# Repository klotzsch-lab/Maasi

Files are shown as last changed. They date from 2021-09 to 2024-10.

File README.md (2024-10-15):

  

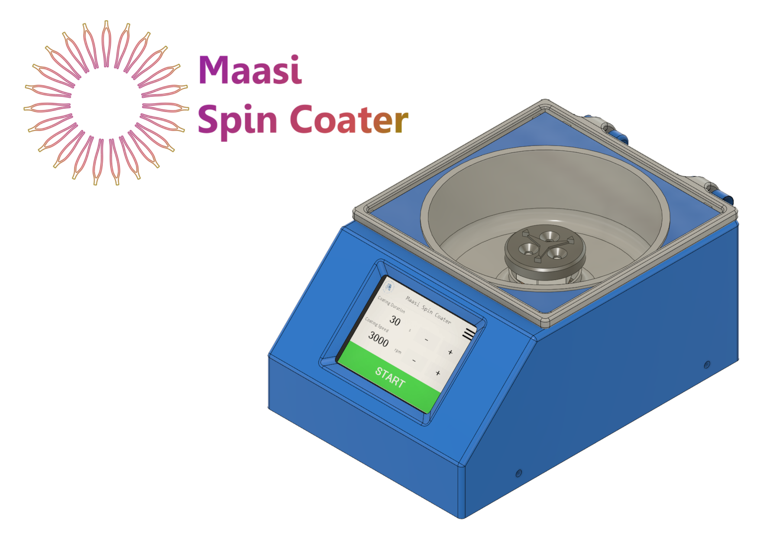
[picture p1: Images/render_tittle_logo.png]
poseidon_logo






## maasi: Open source spin coater

## WARNING!!!!! This project is no longer actively maintained. 

## Proceeding to build or use this project is at your own risk and responsibility.

A fully 3D printed, easy-to-use and open-source spin coater.

**Build tutorial**: https://www.youtube.com/watch?v=bhJrJDhlixs

**HardwareX Paper**: In review

## The tl;dr

Here we present Maasi, an affordable Spin Coater that is easy to build and has all functional key features to be used in a wide range of applications up to 8000 RPM. Our design has a price of approximately 85 € and an assembly time of 2 hours. One of the principles that guided the design was to use only 3D printed parts and affordable Commercial Off-The-Shelf (COTS) components. In order to keep a low part count we use an electronic speed controller (ESC) with telemetry, this eliminates the need for a rotor sensor.

using_maasi

## What is included?

* Computer Aided Design (CAD) files of the complete assembly.

* 3D printable .3MF files.

* Nextion Editor project for the Graphical user interface (GUI).

* Arduino firmware source files.

* Bill of materials for sourcing and purchasing materials.

* Detailed assembly instructions of hardware components.

## Getting Started

### 3D printing components and purchasing hardware

The 3D printed components can be fabricated on any desktop fused filament fabrication (FFF) 3D printer. They were designed using [Autodesk Fusion 360](http://autodesk.com/fusion360), a proprietary CAD software that offers free academic licenses.

- Fusion360 interactive view of [maasi spin coaterCAD](https://a360.co/3xFyf5n).

- Bill of materials with prices and vendor links on a [Spreadsheet](https://github.com/klotzsch-lab/Maasi/tree/main/doc/Maasi-BoM.ods).

- Print files (.3MF ) are available in the [/HARDWARE](https://github.com/klotzsch-lab/Maasi/tree/main/HARDWARE/) folder and print details are specified in the HardwareX publication.

### Build Video

Maasi v1: https://www.youtube.com/watch?v=bhJrJDhlixs&t=412s

Further build instructions are detaild in the HardwareX publication. The following is short version of those instrucitions.

### Setting up the ESP32

The ESP32 is the main MCU in Maasi. It coordinates the actions in the coating process and comunicates with the ESC and the Display MCUs.

Use the Arduino IDE to compile and flash the ESP32 (DevKitc V4)

 <strong>IMPORTANT: </strong> Users are experiencing problems (unresponsive touchscreen) with the Arduino ESP32 [v1.0.5](https://github.com/espressif/arduino-esp32/releases) and above. Please use the Board Manager to install v1.0.4 or previous until a fix is released.

**Make sure to install the following libraries**

-  [Nextion library](https://github.com/klotzsch-lab/Maasi/tree/main/SOFTWARE/Arduino/ITEADLIB_Arduino_Nextion). Included in this repository. To install, unzip the zip file to the libraries sub-folder of your sketchbook, if you get stuck here is a [how-to](https://www.arduino.cc/en/guide/libraries).

-  [PID_V1](https://github.com/br3ttb/Arduino-PID-Library)

-  [ElapsedMillis](https://www.arduino.cc/reference/en/libraries/elapsedmillis/)

### Setting up the Nextion Display

The display project was devoloped using Nextion Editor. We provide precompiled binaries if no customization is needed:

Copy into a micro SD card the file: [maasi_v1.tft](https://github.com/klotzsch-lab/Maasi/tree/main/SOFTWARE/Nextion/maasi_v1.tft)

Install the micro SD card in the Nextion display and power it up.

After the flashing process the SD card can be removed.

### Setting up the BLHeli_32 ESC

The ESC firmware is loaded using [BLHeliSuite32](https://github.com/bitdump/BLHeli/releases)

The required version for this project is the v32.7

An arduino UNO or nano is needed as flashing device between the PC and the ESC.

###  Putting together the Hardware
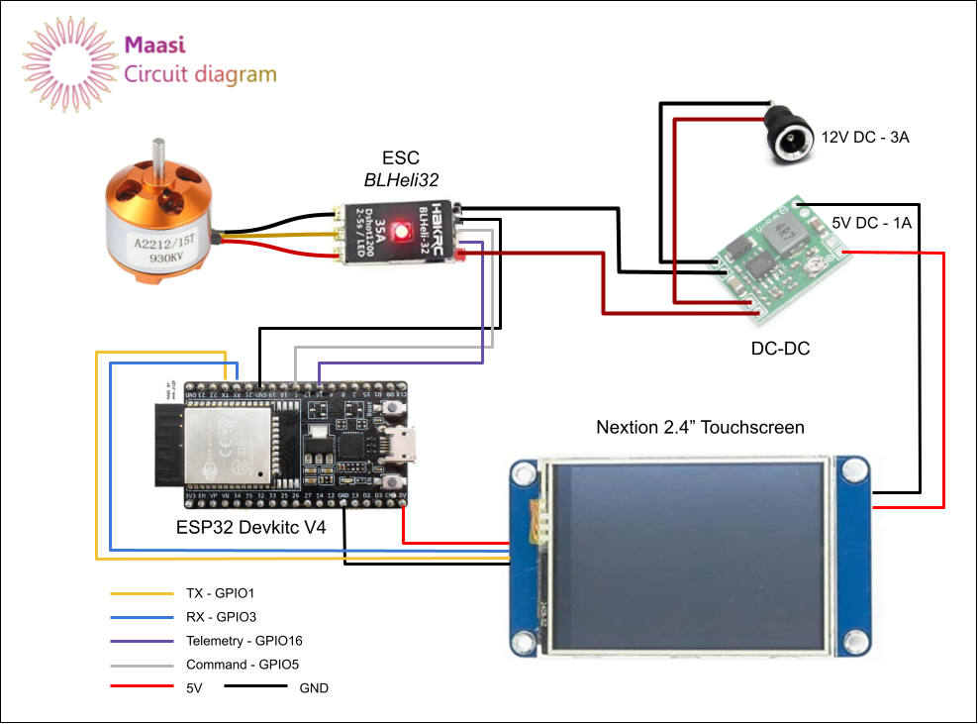
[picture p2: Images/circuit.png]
circuit_diagram_maasi


## Safety Considerations

Please review the license before using/developing/distribution maasi.

The maasi spin coater system uses 3D printed PLA plastic and standard off the shelf components which do not pose a health hazard if handled correctly. Improper handling of plastics however can create hazards when working with organic solvents.

The motor can spin at very high RPM and a safety lid was added to reduce the risk of injure in case that the substrate was not properly fixed to the holder.

Before using maasi in a wetlab environment, please ensure that you have thoroughly tested its functionality for your use case in a dry lab. Once the maasi system has been moved into a wetlab, it should not be moved back to a drylab or dry workbench.

If you plan to build on the maasi spin coater, ensure that you communicate any safety concerns that you may have with your design to potential users and collaborators.

## Authors

Maasi was developed by the [Klotzsch Lab](https://www.biologie.hu-berlin.de/en/groupsites/jpexpbp) at HU Berlin by:

-  [Dani Carbonell](https://github.com/dani-carbonell)

-  Willi Weber

-  [Enrico Klotzsch](https://www.biologie.hu-berlin.de/en/groupsites/jpexpbp/members/Enrico_Klotzsch)

#### Prior work and references

The maasi project is based on a number of other open source projects and papers.
A complete references list can be found inside the HardwareX paper.

The idea to use the ESC telemetry was based on the DIY spin coater built by [@BenKrasnow](https://www.youtube.com/watch?v=321tptQ8PrU) (Applied Science in Youtube)

The documentation format was largely inspired by [Pachter Lab](https://pachterlab.github.io/):

[Booeshaghi, A.S., Beltrame, E.d.V., Bannon, D. et al. Principles of open source bioinstrumentation applied to the poseidon syringe pump system. Sci Rep 9, 12385 (2019). https://doi.org/10.1038/s41598-019-48815-9](https://www.nature.com/articles/s41598-019-48815-9)

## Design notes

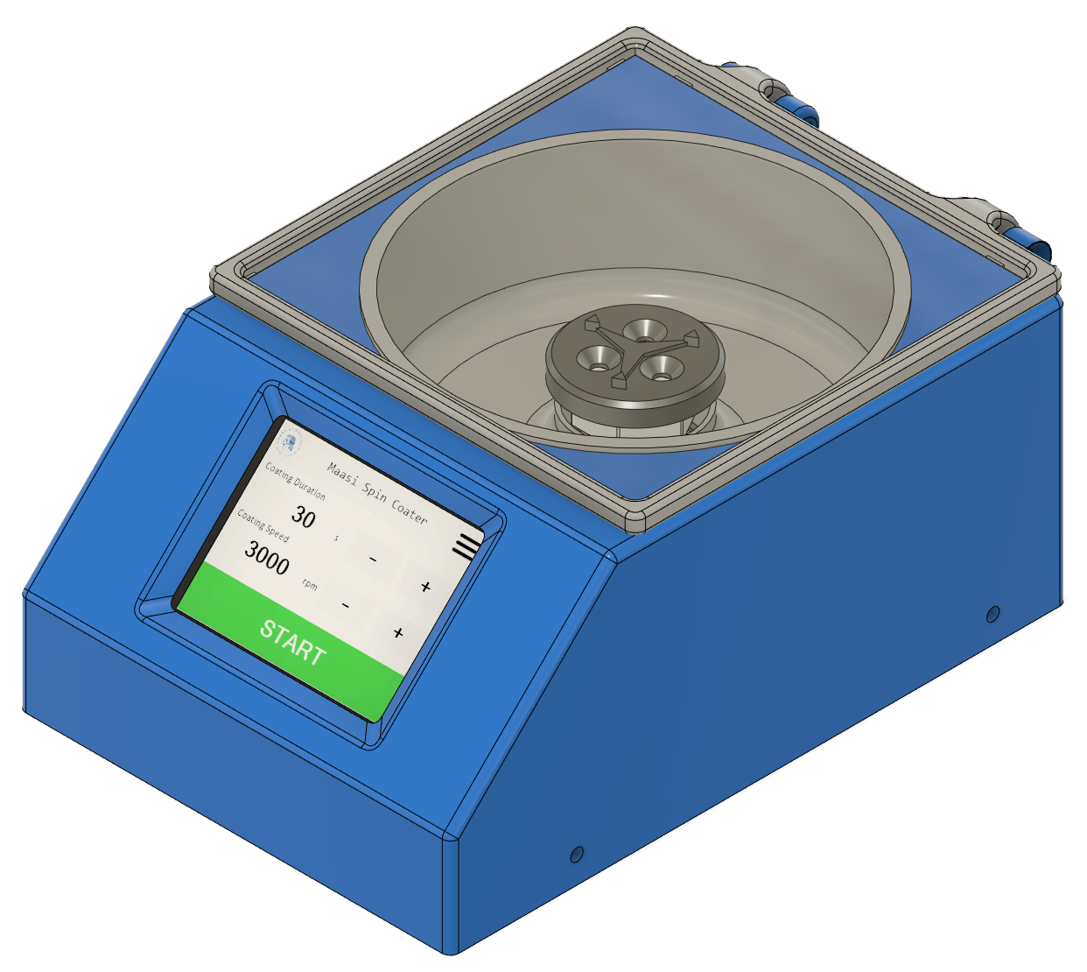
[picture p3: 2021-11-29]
Images/render.png

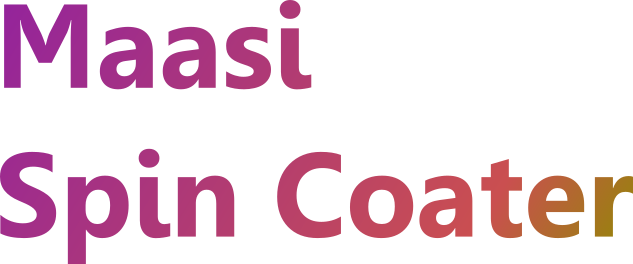
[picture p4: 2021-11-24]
Images/maasi_tittle.png

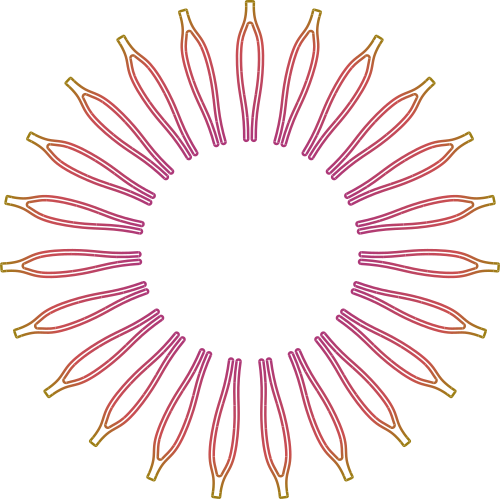
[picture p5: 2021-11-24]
Images/maasi_fusion360_500.png

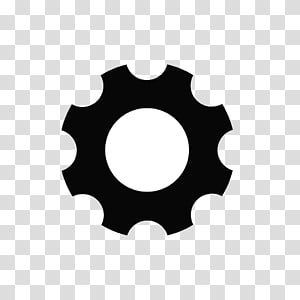
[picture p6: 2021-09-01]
SOFTWARE/Nextion/images/5a95ed98d4fc01607e5e6eb79c2b0c93.jpg

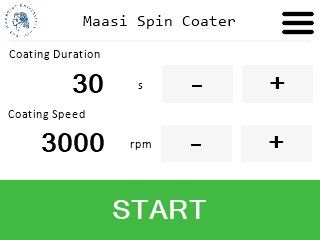
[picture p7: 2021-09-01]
SOFTWARE/Nextion/mainscreen_render.png

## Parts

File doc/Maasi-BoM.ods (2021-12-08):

Designator | Component | Number | Unit | Cost per unit - € | Total cost - € | Source of materials | Material type
PN_001 | BLDC Motor - A2212 - KV930 | 1 |  | 5.87 € | 5.87 € | Aliexpress (https://es.aliexpress.com/item/4001196428994.html) | Composite
PN_002 | ESC - Turnigy MultiStar BLheli_32 ARM 41A | 1 |  | 16.27 € | 16.27 € | HobbyKing (https://hobbyking.com/es_es/turnigy-multistar-32bit-41a-race-spec-esc-2-5s-opto.html?queryID=4c45ede8fe5c60a30a5b7e1fe6d4556b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) | Composite
PN_003 | Mini DC-DC - 12V to 5V | 1 |  | 0.50 € | 0.50 € | Aliexpress (https://es.aliexpress.com/item/32952187058.html) | Composite
PN_004 | ESP32 Devkit v4 | 1 |  | 6.35 € | 6.35 € | Aliexpress (https://es.aliexpress.com/item/1005001838731651.html) | Composite
PN_005 | Nextion NX2432T024 - Touchscreen 2,4" | 1 |  | 23.00 € | 23.00 € | Aliexpress (https://es.aliexpress.com/item/32833690695.html) | Composite
PN_006 | Jack Panel Mount Connector 5.5*2.1mm | 1 |  | 0.70 € | 0.70 € | Aliexpress (https://es.aliexpress.com/item/32985876868.html) | Plastic-Metal
PN_007 | PLA filament | 0.4 | Kg | 20.00 € | 8.00 € | Aliexpress (https://es.aliexpress.com/item/1005003572215645.html) | Plastic
PN_008 | Rubber Feet - 20x16x10mm | 4 |  | 0.18 € | 0.72 € | Aliexpress (https://es.aliexpress.com/item/4000835196671.html) | Rubber-Metal
PN_009 | M3x10 bolts (case) | 4 |  | 0.20 € | 0.80 € | Aliexpress (https://www.aliexpress.com/item/33022099174.html) | Metal
PN_010 | M3x12 bolts (feet) | 4 |  | 0.20 € | 0.80 € | Aliexpress (https://www.aliexpress.com/item/33022099174.html) | Metal
PN_011 | M3x12 bolts (screen) | 4 |  | 0.20 € | 0.80 € | Aliexpress (https://www.aliexpress.com/item/33022099174.html) | Metal
PN_012 | 100x100mm 3mm Transparent Plexiglass | 1 |  | 4.23 € | 4.23 € | Aliexpress (https://www.aliexpress.com/item/4000388406779.html) | Plexiglass
PN_013 | Soldering Tin Lead Free | 5 | g | 0.08 € | 0.42 € | Aliexpress (https://www.aliexpress.com/item/32824531083.html) | Tin
PN_014 | 22AWG Cable (Black-Red) | 0.4 | m | 0.33 € | 0.13 € | Aliexpress (https://www.aliexpress.com/item/4000689875049.html) | Copper-PVC
PN_015 | 12V 5A - AC-DC Power adapter | 1 |  | 10.00 € | 10.00 € | Aliexpress (https://es.aliexpress.com/item/32859196804.html) | Composite
PN_016 | Hook and Loop Fastener Tape 20mm | 0.1 | m | 3.17 € | 0.32 € | Aliexpress (https://es.aliexpress.com/item/33036100627.html) | Nylon
PN_017 | M3 X D4.2 X L5.0 Brass Hot Melt Insert Nuts | 6 |  | 0.08 € | 0.50 € | Aliexpress (https://www.aliexpress.com/item/4000909684199.html) | Metal
PN_018 | M4x20 bolts - Countersunk Head | 2 |  | 0.12 € | 0.24 € | Aliexpress (https://es.aliexpress.com/item/4000020967604.html) | Metal
PN_019 | M3x8 bolts - Countersunk Head | 3 |  | 0.03 € | 0.09 € | Aliexpress (https://es.aliexpress.com/item/4000020967604.html) | Metal
 |  |  |  | TOTAL | 79.73 €
 | Alternatives
Designator | Component | Number | Unit | Cost per unit - EUR | Total cost - EUR | Source of materials | Material type
PN_002_alt1 | ESC - HAKRC BLHeli32 dshot1200 35A | 1 |  | 22.94 € | 22.94 € | Aliexpress (https://es.aliexpress.com/item/4001176494750.html) | Composite
 | Hardware Tools
 | FFF 3D Printer (min. volume 110x160x70mm)
 | Screwdrivers
 | Cutting Pliers
 | Soldering iron
 | Allen Keys
 | Windows 10 Computer with micro SD reader
 | Jumper wires
 | Arduino Uno or Nano
 | Micro SD card
 | Software tools
 | Arduino IDE 1.8
 | BLHeliSuite32
 | Nextion Editor (Optional)
 | Autodesk Fusion 360 (Optional)

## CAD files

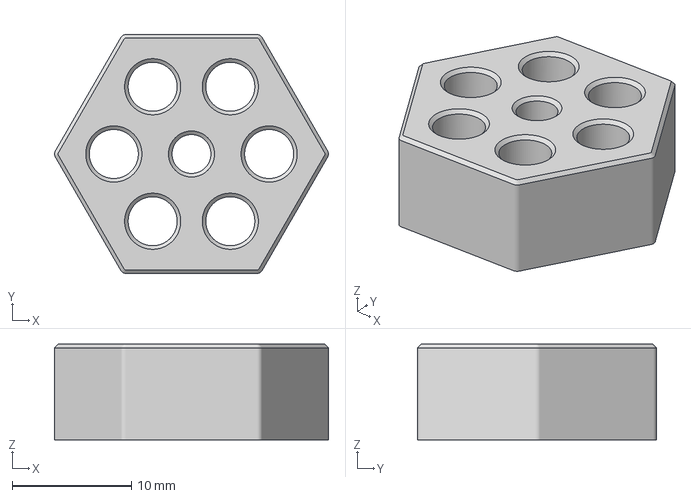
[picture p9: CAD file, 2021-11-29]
HARDWARE/3mf/Shaft_adapter.3mf
22.9 x 20.0 x 8.00 mm

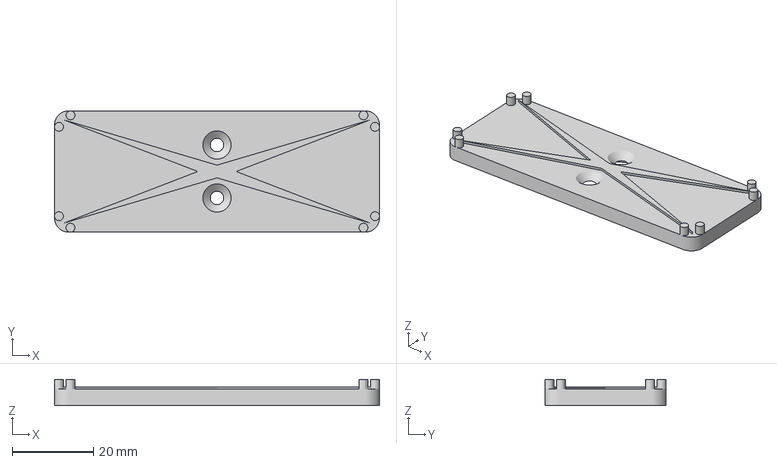
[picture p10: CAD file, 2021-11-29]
HARDWARE/3mf/Square_holder_75x25.3mf
79.8 x 29.8 x 6.40 mm

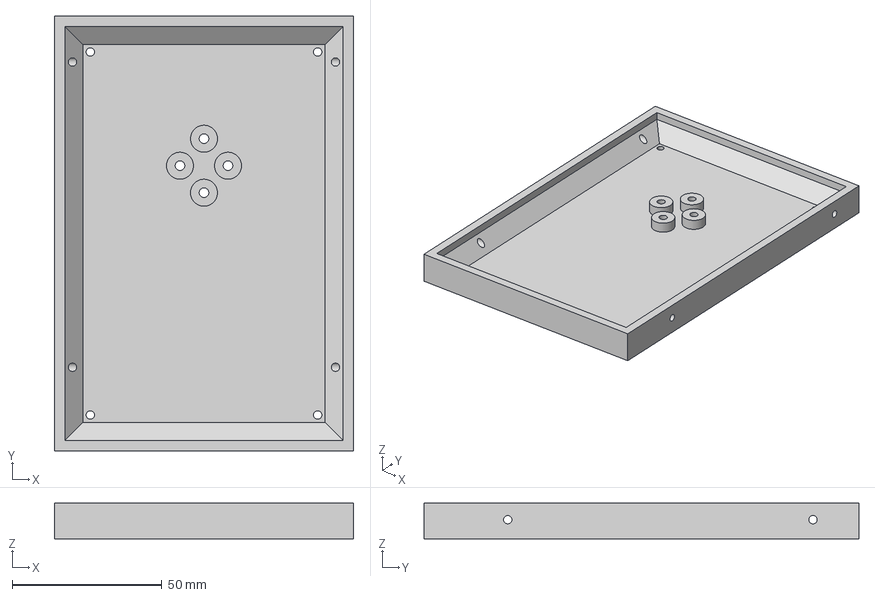
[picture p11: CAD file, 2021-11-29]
HARDWARE/3mf/Base.3mf
99.8 x 145.0 x 12.0 mm

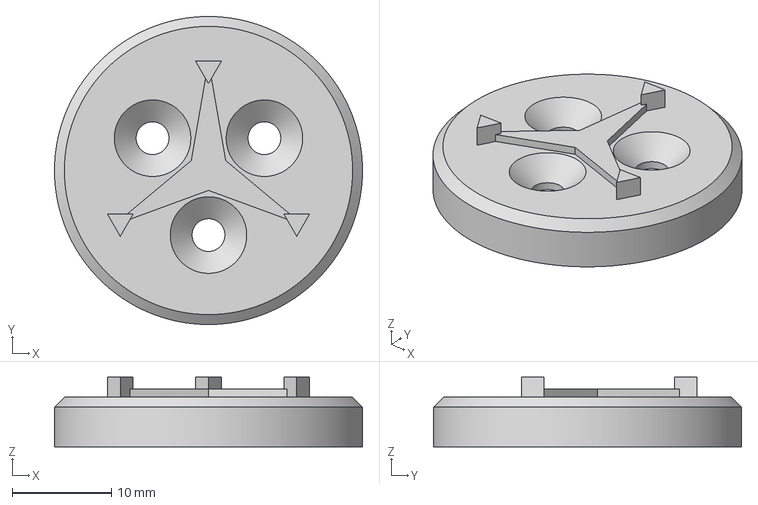
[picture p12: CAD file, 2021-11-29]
HARDWARE/3mf/Round_holder_18mm.3mf
31.0 x 31.0 x 7.00 mm

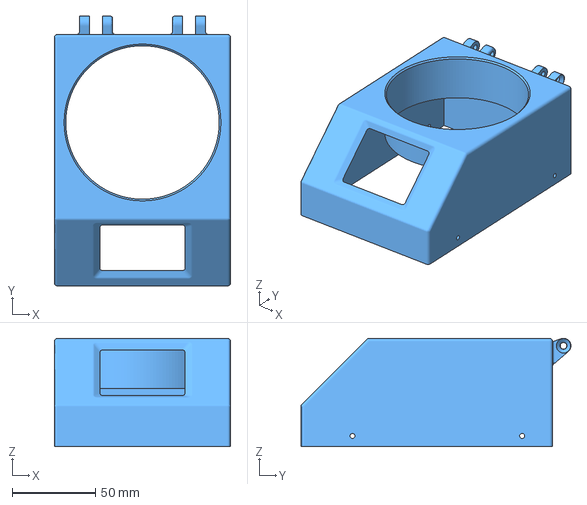
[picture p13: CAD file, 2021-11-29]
HARDWARE/3mf/Case.3mf
105.8 x 162.0 x 65.0 mm

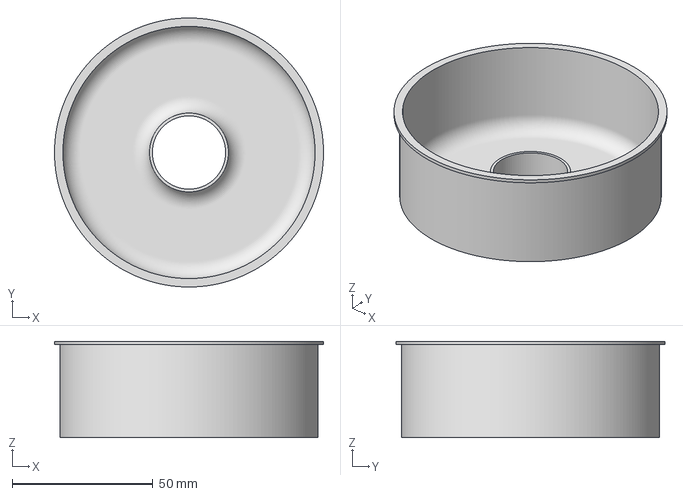
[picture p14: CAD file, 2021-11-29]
HARDWARE/3mf/Vase.3mf
95.5 x 95.5 x 34.2 mm

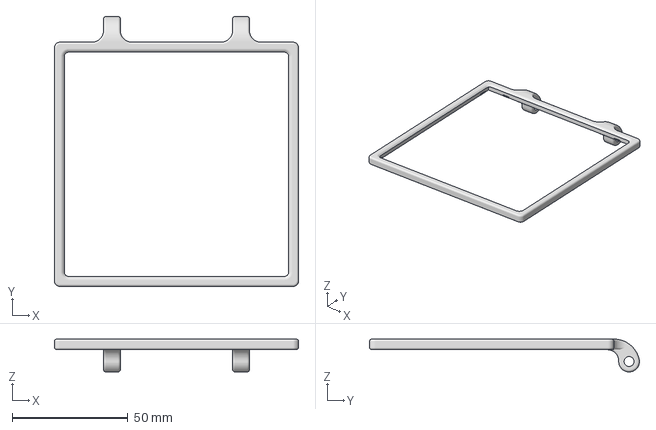
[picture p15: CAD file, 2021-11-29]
HARDWARE/3mf/Lid_frame_hinges.3mf
105.6 x 116.7 x 14.2 mm

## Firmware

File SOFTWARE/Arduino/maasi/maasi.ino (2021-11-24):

#include <HardwareSerial.h>
#include "freertos/FreeRTOS.h"
#include "freertos/task.h"
#include "freertos/event_groups.h"
#include "Arduino.h"
#include "esp32-hal.h"
#include "nextion_hmi.h"
#include <elapsedMillis.h>
#include <PID_v1.h>


#define DEFAULT_DISPENSE_SPEED 600       // RPM
#define DEFAULT_COAT_SPEED 3000          
#define MIN_COAT_SPEED 300
#define MAX_COAT_SPEED 8000
#define INCREMETS_COAT_SPEED 100



#define DEFAULT_COAT_TIME 30000 // In ms
#define MIN_COAT_TIME 1000
#define MAX_COAT_TIME 80000
#define INCREMETS_COAT_TIME 1000
#define DEFAULT_RAMPUP_TIME 3000
#define MIN_RAMPUP_TIME 1000
#define MAX_RAMPUP_TIME 6000
#define DEFAULT_RAMPDOWN_TIME 1500
#define MIN_RAMPDOWN_TIME 500
#define MAX_RAMPDOWN_TIME 5000

#define MOTOR_POLE_PAIRS 7

#define GREY 54970
#define GREEN 17864


//---------------------------------------
//  Coating params
//---------------------------------------

uint16_t disp_speed, coat_speed;

int32_t rampup_time, rampdown_time, coat_time;

enum state {
  STATE_IDLE,
  STATE_DISPENSING,
  STATE_RAMPUP,
  STATE_RAMPDOWN,
  STATE_COATING
};

state current_state, previous_state = STATE_IDLE;

//----------------------------------------------------------------------------
// Espressif Infrared Remote(rmt) library is used to create DSHOT messages in a fast manner
//-----------------------------------------------------------------------------

TaskHandle_t Task1;

rmt_data_t dshotPacket[16];
rmt_obj_t* rmt_send = NULL;

hw_timer_t * timer = NULL;

HardwareSerial TelSerial(1);

// ESC Telemetry variables
uint8_t receivedBytes = 0;
volatile bool requestTelemetry = false;
int16_t ESC_telemetry[5]; // Temperature, Voltage, Current, used mAh, eRpM
//uint32_t telemetry_fails = 0;
//uint32_t telemetry_succ = 0;


uint32_t currentTime;
uint8_t temperature = 0;
uint8_t temperatureMax = 0;
float voltage = 0;
float voltageMin = 99;
uint32_t current = 0;
uint32_t currentMax = 0;
uint32_t erpm = 0;
uint32_t erpmMax = 0;
uint32_t rpm = 0;
uint32_t rpmMAX = 0;
uint32_t kv = 0;
uint32_t kvMax = 0;

//---------------------------------------
//   PID parameters
//---------------------------------------
double motor_setRPM, motor_actualRPM, pid_output = 0;
double pid_out_min = 48;
double pid_out_max = 2047;
double Kp = 0.015, Ki = 0.8 , Kd = 0.0; // Before 1,3,0
const int sample_time = 1; //ms


PID motorPID(&motor_actualRPM, &pid_output, &motor_setRPM, Kp, Ki, Kd, DIRECT);


//---------------------------------------
//   ESC Control Parameters
//---------------------------------------

uint16_t dshotUserInputValue = 0;
uint16_t dshotmin = 48;
uint16_t dshotmax = 2047;

void IRAM_ATTR getTelemetry() {
  requestTelemetry = true;
}

void startTelemetryTimer() {
  timer = timerBegin(0, 80, true); // timer_id = 0; divider=80; countUp = true;
  timerAttachInterrupt(timer, &getTelemetry, true); // edge = true
  timerAlarmWrite(timer, 1000, true);  //1000 = 1 ms
  timerAlarmEnable(timer);
}

// Second core used to send DSHOT packets
void secondCoreTask( void * pvParameters ) {
  while (1) {

    if (requestTelemetry) {
      dshotOutput(dshotUserInputValue, requestTelemetry);
      requestTelemetry = false;
      receivedBytes = 0;
    }

    delay(1);
  }
}

//---------------------------------------
//   Nextion Callbacks
//---------------------------------------


 // START
 
void b1PushCallback(void *ptr)
{
    startDispense();
}

 // STOP
 
void p2b0PushCallback(void *ptr)
{
  if (current_state != STATE_RAMPDOWN){
      startRampdown();    
    }
}

 // COAT
void p2b1PushCallback(void *ptr)
{
  if (current_state == STATE_DISPENSING){
      startRampup();    
    }
}

 // SET BUTTONS
 
void b2PushCallback(void *ptr)
{
   if (coat_time > MIN_COAT_TIME){
    coat_time -= INCREMETS_COAT_TIME;
    }
   n0.setValue(coat_time/1000);

}

void b3PushCallback(void *ptr)
{
    if (coat_time < MAX_COAT_TIME){
    coat_time += INCREMETS_COAT_TIME;
    }
    n0.setValue(coat_time/1000);
}

void b4PushCallback(void *ptr)
{
  if (coat_speed > MIN_COAT_SPEED){
    coat_speed -= INCREMETS_COAT_SPEED;
    }
    n1.setValue(coat_speed);
}

void b5PushCallback(void *ptr)
{
    if (coat_speed < MAX_COAT_SPEED){
    coat_speed += INCREMETS_COAT_SPEED;
    }
    n1.setValue(coat_speed); 
}

void b6PushCallback(void *ptr)
{
    p1.show();
    p1n0.setValue(disp_speed);
    p1n1.setValue(rampup_time/1000);     
    p1n2.setValue(rampdown_time);  
}

void p1b0PushCallback(void *ptr)
{
   if (disp_speed > MIN_COAT_SPEED){
    disp_speed -= INCREMETS_COAT_SPEED/2;
    }
   p1n0.setValue(disp_speed);

}

void p1b1PushCallback(void *ptr)
{
    if (disp_speed < MAX_COAT_SPEED){
    disp_speed += INCREMETS_COAT_SPEED/2;
    }
    p1n0.setValue(disp_speed);
}

void p1b2PushCallback(void *ptr)
{
  if (rampup_time > MIN_RAMPUP_TIME){
    rampup_time -= INCREMETS_COAT_TIME;
    }
    p1n1.setValue(rampup_time/1000);
}

void p1b3PushCallback(void *ptr)
{
    if (rampup_time < MAX_RAMPUP_TIME){
    rampup_time += INCREMETS_COAT_TIME;
    }
    p1n1.setValue(rampup_time/1000); 
}

void p1b4PushCallback(void *ptr)
{
  if (rampdown_time > MIN_RAMPDOWN_TIME){
    rampdown_time -= INCREMETS_COAT_TIME/2;
    }
    p1n2.setValue(rampdown_time);
}

void p1b5PushCallback(void *ptr)
{
  if (rampdown_time < MAX_RAMPDOWN_TIME){
    rampdown_time += INCREMETS_COAT_TIME/2;
    }
    p1n2.setValue(rampdown_time);
}

void p1b6PushCallback(void *ptr)
{

}

void p1b7PushCallback(void *ptr)
{

}
//---------------------------------------
//   Timers
//---------------------------------------
elapsedMillis time_since_display_update = 0;

elapsedMillis time_ramping = 0;
elapsedMillis time_coating = 0;

//elapsedMicros time_since_telemetry = 0;

const int display_update_time = 100;



//---------------------------------------
//   SETUP
//---------------------------------------

void setup() {

  Serial.begin(115200);
  TelSerial.begin(115200, SERIAL_8N1, 16, 17);

  // Init DSHOT hardware
  if ((rmt_send = rmtInit(5, true, RMT_MEM_64)) == NULL) {
    Serial.println("init sender failed\n");
  }

  float realTick = rmtSetTick(rmt_send, 12.5); // 12.5ns sample rate
  //Serial.printf("rmt_send tick set to: %fns\n", realTick);

  // Output disarm signal while esc initialises and do some display stuff.
  uint8_t xbeep = random(15, 100);
  uint8_t ybeep = random(15, 50);
  uint8_t ibeep = 0;
  while (millis() < 3500) {
    dshotOutput(0, false);
    delay(1);

    /// display.clear();
    ibeep++;
    if (ibeep == 100) {
      ibeep = 0;
      xbeep = random(15, 50);
      ybeep = random(15, 50);
    }
  }


  // Empty Rx Serial of garbage telemtry
  while (TelSerial.available()){
    TelSerial.read();
    }
  requestTelemetry = true;
  startTelemetryTimer(); // Timer used to request tlm continually in case ESC rcv bad packet
  xTaskCreatePinnedToCore(secondCoreTask, "Task1", 10000, NULL, 1, &Task1, 0);


  //PID
  coat_speed = DEFAULT_COAT_SPEED;
  disp_speed = DEFAULT_DISPENSE_SPEED;
  coat_time = DEFAULT_COAT_TIME;
  rampup_time = DEFAULT_RAMPUP_TIME;
  rampdown_time = DEFAULT_RAMPDOWN_TIME;
  
  motorPID.SetOutputLimits(pid_out_min, pid_out_max);
  motorPID.SetSampleTime(sample_time);
  
  // Touchscreen init
  nexInit();
  b1.attachPush(b1PushCallback);
  b2.attachPush(b2PushCallback);
  b3.attachPush(b3PushCallback);
  b4.attachPush(b4PushCallback);
  b5.attachPush(b5PushCallback);
  b6.attachPush(b6PushCallback); 
  p1b0.attachPush(p1b0PushCallback);
  p1b1.attachPush(p1b1PushCallback);
  p1b2.attachPush(p1b2PushCallback);
  p1b3.attachPush(p1b3PushCallback);
  p1b4.attachPush(p1b4PushCallback);
  p1b5.attachPush(p1b5PushCallback);
  p1b6.attachPush(p1b6PushCallback);
  p1b7.attachPush(p1b7PushCallback); 
  p2b0.attachPush(p2b0PushCallback);
  p2b1.attachPush(p2b1PushCallback);

  initDisplay();


}


//---------------------------------------
//   LOOP
//---------------------------------------
void loop() {

  nexLoop(nex_listen_list); //Check callback list
  updateDisplay();
  if (!requestTelemetry) {
    motorPID.Compute();
    receiveTelemtry();
  }
  updateMotor();
}

void stopCoating(){
  p0.show();
  current_state = STATE_IDLE;
  }
  
void startDispense(){
  p2.show();
  p2b1.Set_background_color_bco(GREEN); //Set button Green
  t4.setText("Dispense fluid");
  current_state = STATE_DISPENSING;
  
  motor_setRPM = disp_speed;
  motorPID.SetMode(AUTOMATIC); 
  }
  
void startRampup(){
  p2b1.Set_background_color_bco(GREY); //Set button Grey
  t4.setText("Ramping up");
  current_state = STATE_RAMPUP;
  
  motorPID.SetMode(AUTOMATIC);
  time_ramping = 0;
  }
  
void startRampdown(){
  t4.setText("Ramping down");
  current_state = STATE_RAMPDOWN;
  
  motorPID.SetMode(AUTOMATIC);
  time_ramping = 0; 
  }
  
void startCoating(){
  //p2.show();
  //p2b1.Set_background_color_bco(GREY); //Set button Grey
  t4.setText("Coating");
  current_state = STATE_COATING;
 
  motor_setRPM = coat_speed; 
  motorPID.SetMode(AUTOMATIC); 
  time_coating = 0;
  }

void initDisplay(){
    n0.setValue(coat_time/1000);
    n1.setValue(coat_speed);
    p1n0.setValue(disp_speed);
    p1n1.setValue(rampup_time/1000);
    p1n2.setValue(rampdown_time);
  }

void updateDisplay() {

  if (time_since_display_update >= display_update_time) {
    time_since_display_update = 0;

    switch (current_state){
      case STATE_IDLE:  
        break;
        
      case STATE_DISPENSING:
        p2n0.setValue(coat_time/1000);
        p2n1.setValue(motor_actualRPM);
        p2j0.setValue(0);
        break;
      case STATE_RAMPUP:      
        p2n0.setValue((rampup_time - time_ramping)/1000);
        p2n1.setValue(motor_actualRPM);
        //p2j0.setValue(100-(rampup_time - time_ramping)*100/rampup_time);
        break;      
      case STATE_RAMPDOWN:      
        p2n0.setValue((rampdown_time - time_ramping)/1000);
        p2n1.setValue(motor_actualRPM);
        p2j0.setValue(0);
        break;     
      case STATE_COATING:      
        p2n0.setValue((coat_time - time_coating)/1000);
        p2n1.setValue(motor_actualRPM);
        p2j0.setValue((coat_time - time_coating)*100/coat_time); // % Progress bar
        //p2n0.setValue(abs(coat_speed - motor_actualRPM)); //Debuging RPM error 
        break;
    } 
  }
}


void updateMotor() {

    motor_actualRPM = rpm;

    
    switch (current_state){
      case STATE_IDLE:
       motorPID.SetMode(MANUAL); 
       dshotUserInputValue = 0;
       pid_output = 0;    
       break;
        
      case STATE_DISPENSING:
        dshotUserInputValue = pid_output;
        break;
        
      case STATE_RAMPUP:
        if (time_ramping < rampup_time){
          motor_setRPM = map(time_ramping, 0, rampup_time, disp_speed, coat_speed);
          dshotUserInputValue = pid_output;     
          }
        else{
          startCoating();
          }     
        break;
        
      case STATE_COATING:
        if (time_coating < coat_time){
          dshotUserInputValue = pid_output;    
          }
        else{
          startRampdown();
          }     
        break;

      case STATE_RAMPDOWN:
        int rampdown_speed = motor_actualRPM;
        if (time_ramping < rampdown_time){
          motor_setRPM = map(time_ramping, 0, rampdown_time, rampdown_speed, 0 );
          dshotUserInputValue = pid_output;     
          }
        else{
          stopCoating();
          }     
        break;

    }

}
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

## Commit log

2021-09-01 First code added
    [slide_holder_20mm.3mf]
2021-11-29 Documentation images and dessign files added
    [Base.3mf, Case.3mf, Lid_frame_hinges.3mf, Round_holder_18mm.3mf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]
2021-12-07 Release Nextion files and BoM
    [Maasi-BoM.ods]
2021-12-07 Almost finished
    [Maasi-BoM.ods]
